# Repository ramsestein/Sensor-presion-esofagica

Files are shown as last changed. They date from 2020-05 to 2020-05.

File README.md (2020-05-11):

# **Open-Source Transpulmonary Pressure Sensor**

Arduino-based Transpulmonary pressure monitoring portable device project:  Open-Source Transpulmonary Pressure Sensor.

This Open-Source Transpulmonary Pressure Sensor (OSTPS) allows for rapid measuring of Transpulmonary Pressure (PL)
through airway pressure (Paw) and esophageal pressure (Pes) capture on intubated patients,
particularly those affected by bilateral pneumonia due to SARS-COV-2, pressures are measured using the respiratory cannula  
for Paw and an esophageal balloon nasogastric probe for Pes.

The OSTPS's accuracy in this first iteration is +-0.18cmH2O (theorical) so its reliability and precision is assumed correct for this type of measurement.

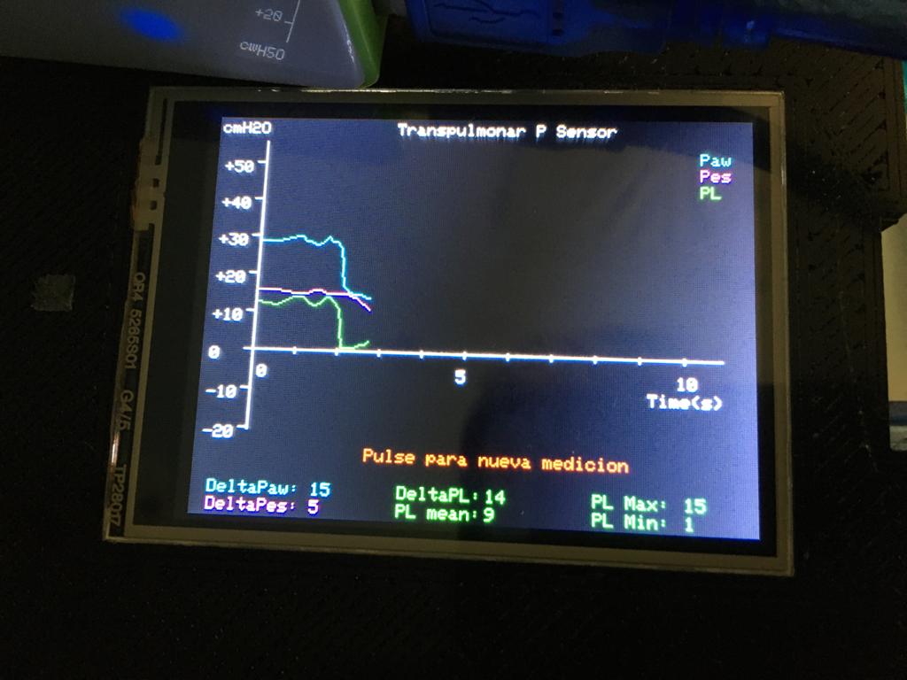
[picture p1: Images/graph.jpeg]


**The use of a OSTPS must be performed by trained medical personnel.**

Mechanical ventilation monitoring, at its basis, encompasses airway pressure and flow.
For most patients, these two measurements are enough to perform ventilation adjustments. 
However, airway pressure is only the resulting measurement of pressures at play in the main respiratory system's components:
lungs and chest wall (simplified).

To perform precise adjustments of mechanical ventilation or evaluating lung recruitability in acutely ill patients,
differentiating these two components compliance is necessary.

It's assumed esophageal pressure (Pes) is representative of pleural pressure*.

Through Paw and Pes measurement it is possible to obtain Transpulmonary Pressure (PL)=Paw-Pes measured
during occlusion at end inspiration and expiration. PL represents the necessary pressure to dilate the lung parenchyma.
This first OSTPS version also calculates Paw and Pes differentials.

Through the use of OSTPS clinicians may get a better perception of patient-ventilator interaction and plan for respiratory strategy
more accurately.

## Problem

PL monitorization is an already existing technology only implemented in most modern mechanical respirators.

Pressure measurements necessary to calculate PL can be obtained with most electromedical devices nonetheless.
Although, this data acquisition without integrated calculation tools is a lengthy process,
demanding a span of time medical personnel can't spare given the high occupancy rate and hard hygiene measures,
as happens with SARS-COV-2 affected patients.

We propose a Transpulmonary Pressure Sensor model, based on Arduino, easy to build and portable.
This prototype can be produced in short time with off the shelf components, and allows medical personnel to correctly asses acutely ill patients,
giving them supplementary room for improvement which may be crucial for recovery in the most critical cases.

The development of this project is based on already existing pressure sensors/transducers, which may be hard to come by given the actual market situation.
We recommend consulting with target medical personnel the need for a OSTPS before sourcing components to avoid a colapse in supply.
Not all medical personnel is familiar with PL monitoring and its implications for mechanical ventilation, this is a fairly recent technique.

Nonetheless this now very accessible technology can help save lives if used correctly,
especially for those acutely ill patients who need more advanced mechanical ventilation monitoring.

### References
1. Talmor D, Sarge T, O’Donnell C, Ritz R, Malhotra, Lisbon A, Loring S. Esophageal and transpulmonary pressures in acute respiratory failure Crit Care Med 2006; 34:1389–1394
2. Gattinoni L, Chiumello D, Carlesso E, Valenza F. Benchto-bedside review: Chest wall elastance in acute lung injury/acute respiratory distress syndrome patients. Critical Care 2004, 8:350-355
3. Hess D, Bigatello L. The chest wall in acute lung injury/acute respiratory distress syndrome. Curr Opin Crit Care 2008;14:94–102
4. Akoumianaki E, Maggiore S, Valenza F, Bellani G, Jubran A, et al. The application of esophageal pressure measurement in patients with respiratory failure. Am J Respir Crit Care Med 2014;189:520-31

### Made possible by
Francisco José Parrilla Gómez - Critical Care Medicine specialist physician, Intensive Medicine Service, Hospital del Mar, Parc de Salut Mar, IMIM, GREPAC, Barcelona - concept, development, clinical advisor, testing  
Andrés Parrilla Gómez - Lycée Saint Stanislas, Nantes - concept, development, programming  
Alvaro Jansà - Fablab Sant Cugat, Barcelona - development, production, programming support  
Marc Estudillo - Electromedical Engineering, Barcelona - development, production  
Victor Boutonnet Antelo - Benimakers Makerspace, Valencia - development, programming support, project coordination  

Made available under Creative Commons Licence Attribution 4.0 International (CC BY 4.0).

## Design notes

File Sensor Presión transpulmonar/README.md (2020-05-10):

# **Sensor de Presión Transpulmonar Open-Source**

Proyecto de herramienta portatil de medición de la presión transpulmonar basada en arduino: Sensor de Presión Transpulmonar Open-source.

El Sensor de Presión Transpulmonar Open-Source (SPTO) permite la rápida medición de la presión transpulmonar (PL)
mediante captación de presión en vía aérea (Paw) y en vía esofágica (Pes) en pacientes intubados,
particularmente afectados de neumonía bilateral por SARS-COV-2, empleando la propía cánula respiratoria  
para la medición de Paw y una sonda nasogástrica con balón esofágico para la medición de Pes.

La precisión del SPTO en su primera versión es de +-0.18cmH2O (teórica) por lo que se comprueba fiabilidad para éste tipo de mediciones.

**El uso del SPTO debe ser realizado por personal médico competente en la materia.**

Aunque técnicamente no sea necesario, éste aparato no ha sido validado por la AEMPS.

La monitorización de la ventilación mecánica comprende como base la presión en vía aérea y el flujo.
Para la mayoría de pacientes, éstas dos medidas son suficientes para realizar los ajustes de ventilación. 
Sin embargo, la Presión en vía aérea es sólo una medición indirecta de las presiones en juego
en los componentes principales del sistema respiratorio (simplificando): pulmones y caja torácia.

Para realizar un ajuste preciso de la ventilación mecánica o evaluar la capacidad de reclutamiento pulmonar de los pacientes más graves,
se hace necesario diferenciar la complianza de ambos.

Está asumido que la medición de la Presión Esofágica (Pes) es un buen indicador que sustituye la medición de la presión pleural*.

Mediante la medición de la Paw y la Pes es posible obtener la presión transpulmonar(PL)=Paw-Pes calculada
durante la oclusión en fin de inspiración y espiración. PL representa la presión necesaria para dilatar el parénquima pulmonar.
El SPTO calcula también los diferenciales de Paw y Pes durante la medición.

De éste modo el personal médico tiene una mejor percepción del efecto de la ventilación mecánica y/o de la capacidad de reclutamiento pulmonar del paciente,
pudiendo realizar ajustes precisos del modo ventilatorio.

*Referencias:
1. Talmor D, Sarge T, O’Donnell C, Ritz R, Malhotra, Lisbon A, Loring S. Esophageal and transpulmonary pressures in acute respiratory failure Crit Care Med 2006; 34:1389–1394
2. Gattinoni L, Chiumello D, Carlesso E, Valenza F. Benchto-bedside review: Chest wall elastance in acute lung injury/acute respiratory distress syndrome patients. Critical Care 2004, 8:350-355
3. Hess D, Bigatello L. The chest wall in acute lung injury/acute respiratory distress syndrome. Curr Opin Crit Care 2008;14:94–102
4. Akoumianaki E, Maggiore S, Valenza F, Bellani G, Jubran A, et al. The application of esophageal pressure measurement in patients with respiratory failure. Am J Respir Crit Care Med 2014;189:520-31

#Problemática:

La monitorización de PL es una tecnología que ya incluyen sólo algunos de los ventiladores mecánicos más modernos.

No obstante, las medidas de presión necesarias al cálculo de PL se pueden tomar con la mayoría de equipos electromédicos ya existentes.
Sin embargo, la toma de medidas sin herramientas de cálculo integradas supone un proceso demasiado largo de toma de datos y procesado de los mismos:
un tiempo del que el personal médico no dispone en situación de alta ocupación sumada a medidas de higiene extremas,
como ocurre con los pacientes afectados por SARS-COV-2.

Proponemos un modelo de sensor de presión transpulmonar, portátil y de fácil fabricación basado en Arduino.
Éste prototipo se puede fabricar en poco tiempo con componentes off the shelf y supone dar capacidad al personal médico para monitorizar los pacientes más graves
dándoles un margen de mejora que puede resultar crucial en los casos más críticos.

El desarrollo está basado en torno a sensores/transductores de presión disponibles en el mercado, aunque difíciles de conseguir en las circunstancias actuales.
Recomendamos consultar con personal médico la necesidad de contar con un SPTO antes de realizar compra de material si se va a fabricar una unidad.
No todo el personal médico está familiarizado con la monitorización de la PL y su implicación para la mecánica respiratoria.

No obstante es una tecnología muy accesible que puede ayudar a salvar vidas si se emplea debidamente,
especialmente en aquellos pacientes más graves que necesitan de una monitorización más avanzada de la ventilación mecánica.

Creado por:
Francisco José Parrilla Gómez - Médico especialista en Medicina Intensiva, Servicio de Medicina Intensiva, Hospital del Mar, Parc de Salut Mar, IMIM, GREPAC, Barcelona - concepto, desarrollo, consejo clínico, pruebas
Andrés Parrilla Gómez - Lycée Saint Stanislas, Nantes - concepto, desarrollo, programación
Alvaro Jansà - Fablab Sant Cugat, Barcelona - desarrollo, producción, soporte programación
Marc Estudillo - Ingeniería electromédica, Barcelona - desarrollo, producción
Victor Boutonnet Antelo - Benimakers Makerspace, Valencia - desarrollo, soporte programación, coordinación proyecto

Liberado bajo Licencia Creative Commons Atribución 4.0 Internacional.

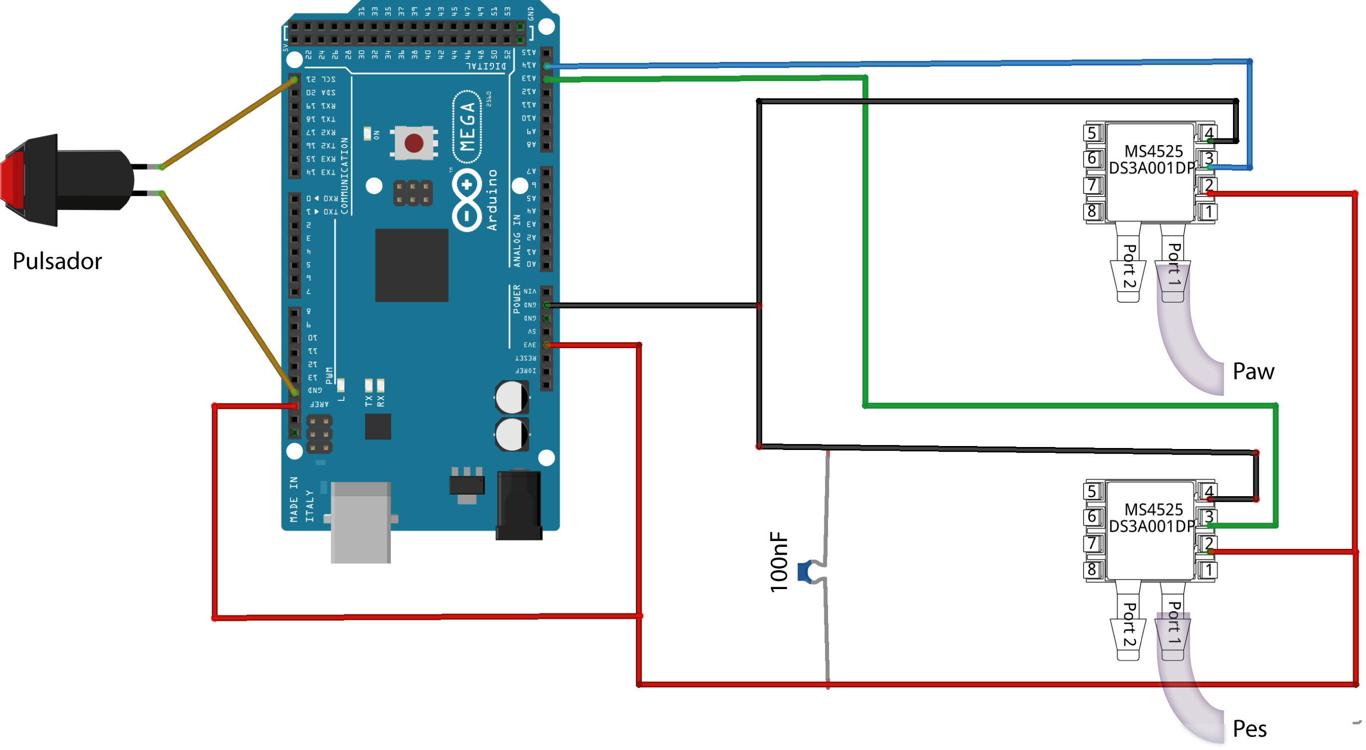
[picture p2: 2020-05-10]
Schematics/Sensor_P_TransP.png

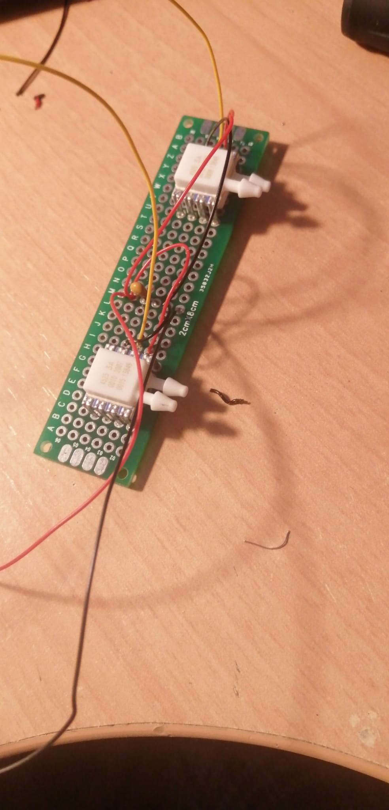
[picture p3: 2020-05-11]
Images/2020-05-01 at 11.52.09.jpeg

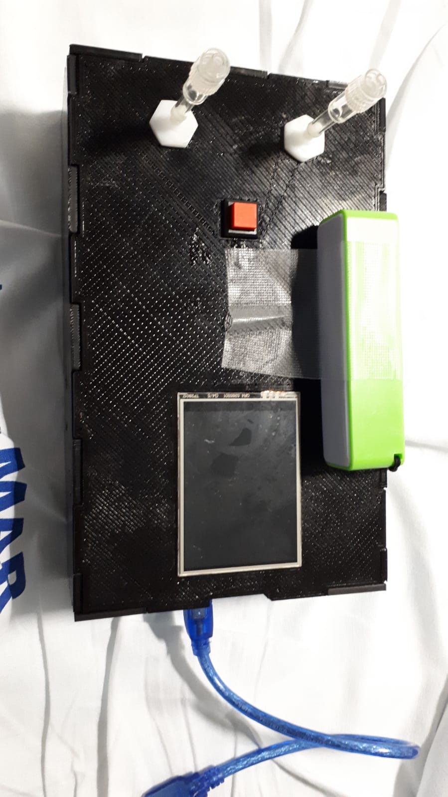
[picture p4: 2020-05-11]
Images/2020-05-06 at 07.55.35.jpeg

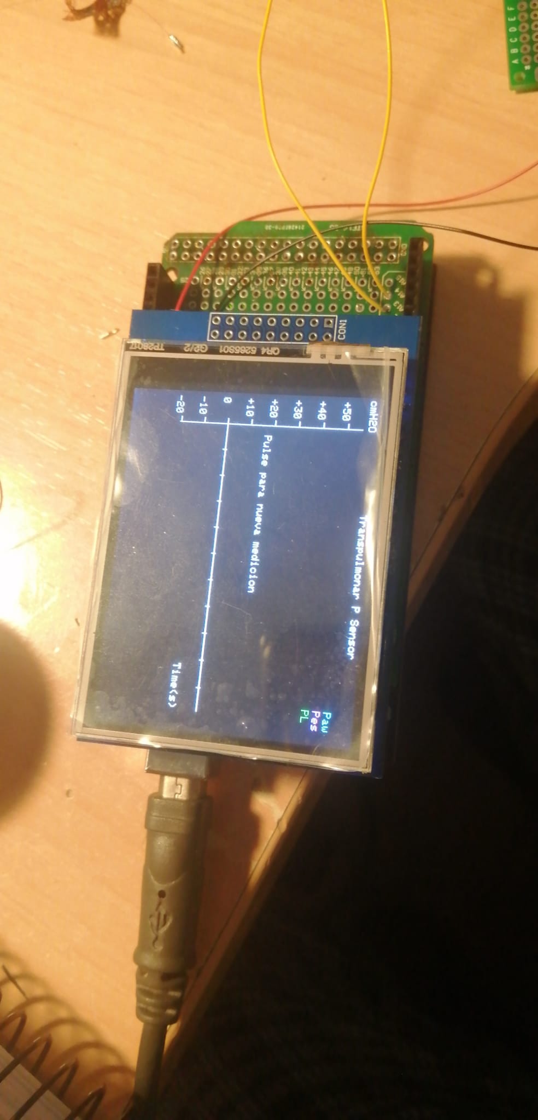
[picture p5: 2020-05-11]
Images/2020-05-01 at 11.52.01.jpeg

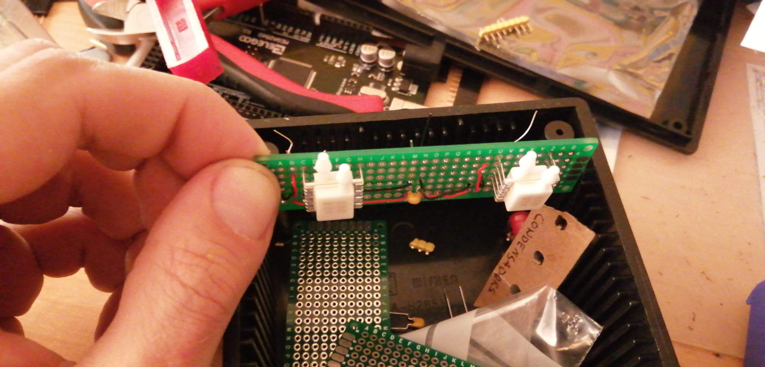
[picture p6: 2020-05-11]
Images/2020-04-30 at 22.00.41.jpeg

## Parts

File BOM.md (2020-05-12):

Arduino Mega    x 1
Arduino Mega Proto Shield Rev3 (PCB)    x 1
Protoshield 3x7cm      x 1
ELEGOO UNO R3 2.8 Inches TFT Touch Screen    x 1
Pulsador     x 1
Capacitador ceramico 100nf     x 1
Sensor presion MS4525     x 2
Tubos XX (interior)     x 2
Adaptadores (int-ext)XX      x 2
Adaptador YY (ext)     x 2

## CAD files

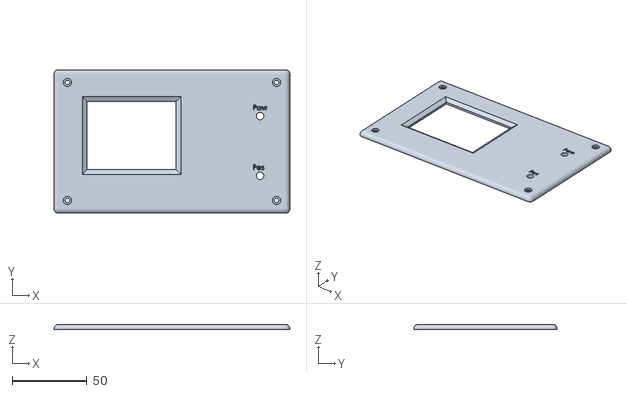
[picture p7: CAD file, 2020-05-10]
CAD/tapa_caja_v0.3.STL
158.0 x 96.0 x 3.50

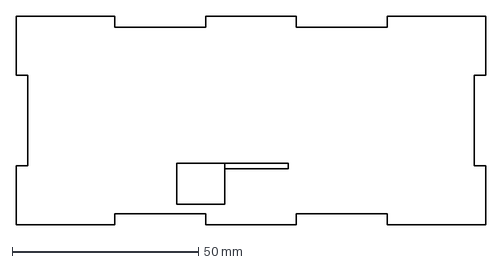
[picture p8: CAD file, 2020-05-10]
CAD/front_makercase_laser_v0.1.DXF
126.0 x 56.0 mm

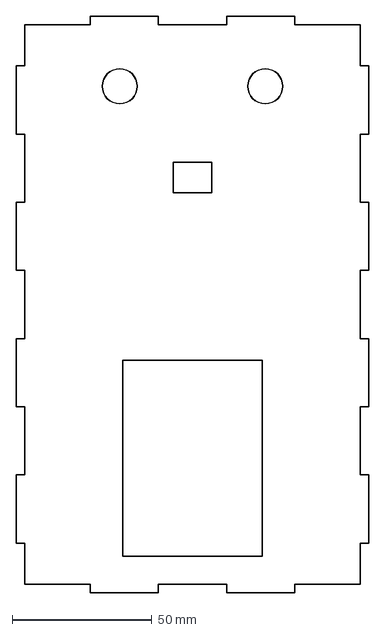
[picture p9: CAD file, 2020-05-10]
CAD/tapa_makercase_laser_v0.1.DXF
126.0 x 206.0 mm

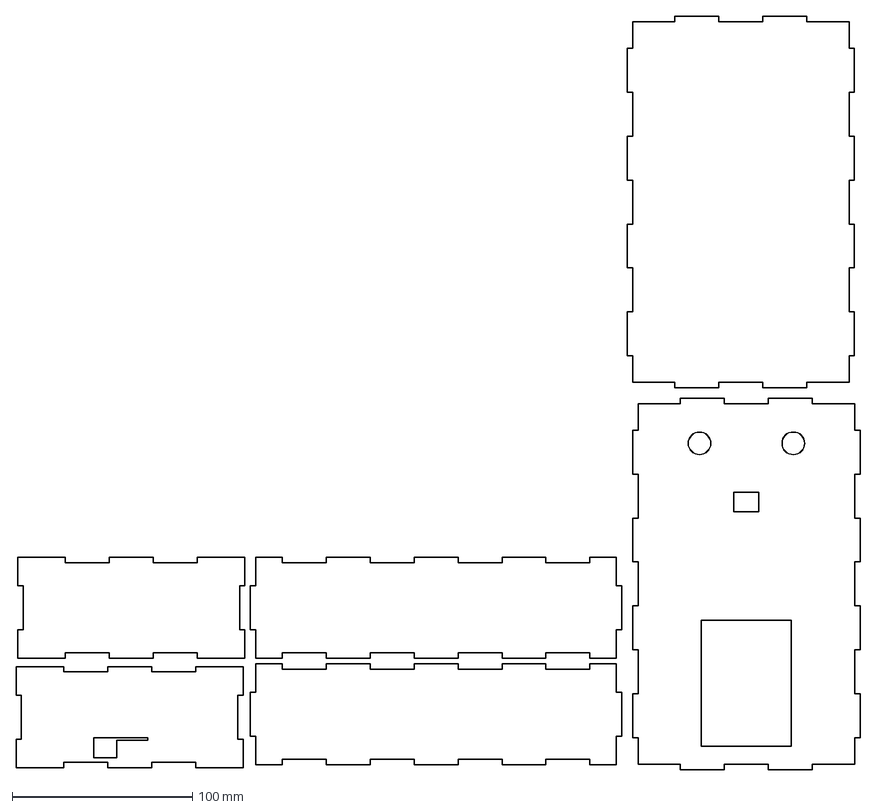
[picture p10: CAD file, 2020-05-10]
CAD/makercase_laser_todo_v0.1.DXF
468.0 x 417.8 mm

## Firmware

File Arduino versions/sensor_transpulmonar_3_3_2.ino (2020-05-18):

/*
Transpulmonar sensor
 version 3.3.4
 
 Authors:
 Francisco Jose PARRILLA GOMEZ
 Alvaro JANSA MAS
 Marc ESTUDILLO
 Victor BOUTONNET ANTELO
 Andres PARRILLA GOMEZ
 
 Description:
 Transpulmonar sensor using 2 pressure sensors, Arduino MEGA and TFT LCL Elegoo 2.8" touchscreen
 
 modifs:
 v1 2020-04-27 : initial version
 v2 2020-04-30 : analog reference to 3.3V, TFT added, compiler options and bug correction
 v3.0 2020-05-02 : graphics improvements
 v3.1 2020-05-02 : bug corrections
 v3.1.1 2020-05-02 : more bug corrections
 v3.1.2 2020-05-03 : graphics improvements
 v3.2 2020-05-04 : graphics improvements
 v3.3 2020-05-04 : round values to integers (round to 0.5 commented out)
 v3.3.1 2020-05.06 : back to float values
 v3.3.2 2020-05.06 : rounding compiler options added
 v3.3.3 2020-05-09 : changed PL avg to Ratio
 v3.3.4 2020-05-09 : bug fix
 */




// User defined compiling parameters
// *********************************
#define ARDUINOBOARD 'M' // must be 'U' for UNO or 'M' for MEGA. Warning: with UNO, fake values!
#define DEBUG 0 // must be 0 or 1
#define USERCOM 'B' // must be 'B' for BUTTON, 'S' for SERIAL or 'T' for TOUCHSCREEN ( TOUCHSCREEN TODO: not working as of 2.6)
#define ROUNDOPTION 0 //must be 1 to integer values, 5 for .5 rounding or 0 for max resolution
// *********************************





// TFT
#include <Elegoo_GFX.h>
#include <Elegoo_TFTLCD.h>
//#include <stdint.h>
#include <TouchScreen.h>

#define LCD_CS A3
#define LCD_CD A2
#define LCD_WR A1
#define LCD_RD A0
#define LCD_RESET A4
#define YP A1
#define XM A2
#define YM 7
#define XP 6

#define GREY    0x8410
#define BLACK   0x0000
#define BLUE    0x001F
#define RED     0xF800
#define GREEN   0x07E0
#define CYAN    0x07FF
#define MAGENTA 0xF81F
#define YELLOW  0xFFE0
#define WHITE   0xFFFF

#define MINPRESSURE 10
#define MAXPRESSURE 1000

#if USERCOM=='S'
#define DEBUG 1
#endif

Elegoo_TFTLCD tft(LCD_CS, LCD_CD, LCD_WR, LCD_RD, LCD_RESET);
#if USERCOM=='T'
TouchScreen ts = TouchScreen(XP, YP, XM, YM, 300);
#endif

// Pin definitions
#if ARDUINOBOARD=='M'
const int PesPin(A13);
const int PawPin(A14);
#endif

#if USERCOM=='B'
const int buttonPin = 21; // Warning, I2C pin too...
unsigned long timeButton(0);
#endif

// Sensors characteristics
int PesVDefaultOffset(512);
int PawVDefaultOffset(512);
int PesVOffset(PesVDefaultOffset); 
int PawVOffset(PawVDefaultOffset);

// gain definitions for class A TE sensors (MS4525 - DS3A001DP)
//for 3V supply and AREF=3.3V
float PesGain(70.31/409); //1 psi = 70,31 cmH2O
float PawGain(70.31/409);

//Data treatment parameters
int nMeasures(10); // number of measures to average (low-cost filtering...)
float precision(0.);
int tmp(0.);

//current values
int PesV(0); // V stands for Volts (direct tension measured)
int PawV(0);
int PesVtmp(0);
int PawVtmp(0);
int PesVmax(0);
int PesVmin(1023);
int PawVmax(0);
int PawVmin(1023);
float Pes(0.);
float Paw(0.);
float PL(0.);
float PLmax(0.);
float PLmin(0.);
float PLavg(0.);
float Pesmax(0.);
float Pesmin(0.);
float Pawmax(0.);
float Pawmin(0.);
int counterMeasures(0);

// behavior variables
bool measuring=false;
//TSPoint tcPoint;

// plotting variables
int HPos (31+250); // pixel corresponding to time=0 + plotting area width
int lastHPos(31+250);

unsigned int Pes2plot(0);
unsigned int Paw2plot(0);
unsigned int PL2plot(0);
unsigned int lastPes2plot(0);
unsigned int lastPaw2plot(0);
unsigned int lastPL2plot(0);

// time variables
float tini(0); //measure start time
float tcurrent(0); //measure start time
int screenNumber(0); // times screen erased and shown again (multiples of 10s)

void setup() {

  // Touchscreen ini
  tft.reset();
  tft.begin(0x9341);
  tft.fillScreen(BLACK);
  tft.setRotation(1);

#if DEBUG==1 || USERCOM=='U'
  Serial.begin(9600);
  pinMode(13,OUTPUT);
  digitalWrite(13,LOW);
#endif

#if USERCOM=='B'
  pinMode(buttonPin, INPUT_PULLUP);
#if ARDUINOBOARD=='M'
  attachInterrupt(2, buttonPressed, FALLING); // 2 stands for pin 21 (number 2 of Mega board interrupts)
#elif ARDUINOBOARD=='U'
  tft.fillScreen(BLACK);
  tft.setCursor(40,100);
  tft.println("ERROR:Opotions defined are not compatible (UNO board with BUTTON communication");
#endif
#endif



  // Pressure sensors autozero
  analogReference(EXTERNAL);
#if ARDUINOBOARD=='M'
  pinMode(PesPin, INPUT);
  pinMode(PawPin, INPUT);
#endif

  PesVtmp=0;
  PawVtmp=0;
  PesVmax=0;
  PesVmin=1023;
  PawVmax=0;
  PawVmin=1023;
  PesVOffset=0;
  PawVOffset=0;
  for(int i = 0; i < nMeasures; i++){
#if ARDUINOBOARD=='M'
    PesVtmp=analogRead(PesPin);
    PawVtmp=analogRead(PawPin);
#elif ARDUINOBOARD=='U'
    PesVtmp=512+int(random(-3,4)); //UNO fake values
    PawVtmp=520+int(random(-3,4)); //UNO fake values
#endif
    PesVOffset+=PesVtmp;
    PawVOffset+=PawVtmp;
    PesVmax=max(PesVmax,PesVtmp);
    PesVmin=min(PesVmin,PesVtmp);
    PawVmax=max(PawVmax,PawVtmp);
    PawVmin=min(PawVmin,PawVtmp);
    delay(10);
  }
  PesVOffset=PesVOffset/nMeasures;
  PawVOffset=PawVOffset/nMeasures;

#if DEBUG==1
  Serial.println("AUTOZERO");
  if(abs(PesVOffset-PesVDefaultOffset)>50){
    Serial.print("Warning: check autozero for Pes");
  }
  Serial.println("PesVOffset="+String(PesVOffset));
  if(abs(PawVOffset-PawVDefaultOffset)>50){
    Serial.print("Warning: check autozero for Paw");
  }
  Serial.println("PawVOffset="+String(PawVOffset));
  if(PesVmax-PesVmin>50){
    Serial.print("Warning: instable measures of Pes: max="+String(PesVmax)+" ; min="+String(PesVmin));
  }
  if(PawVmax-PawVmin>50){
    Serial.print("Warning: instable measures of Paw: max="+String(PawVmax)+" ; min="+String(PawVmin));
  }
#endif

  tft.setCursor(20,100);
  tft.setTextColor(WHITE);
  tft.setTextSize(2);
  tft.println("Autozero done");
  tft.setCursor(20,120);
  tft.setTextSize(1);
  precision=max(max(PesGain*float(PesVmax-PesVmin),PawGain*float(PawVmax-PawVmin)),0.2);
  tft.println("precision:+- "+String(round(precision*10.)/10)+"."+String(round(precision*10.)%10)+" cmH2O");
#if DEBUG==1
  Serial.print("PesVmax: ");
  Serial.println(PesVmax);
  Serial.print("PesVmin: ");
  Serial.println(PesVmin);
  Serial.print("PawVmax: ");
  Serial.println(PawVmax);
  Serial.print("PawVmin: ");
  Serial.println(PawVmin);
  Serial.print("precision: ");
  Serial.println(precision);
  Serial.print("round(precision*10.)/10: ");
  Serial.println(round(precision*10.)/10);
  Serial.print("round(precision*10.)%10: ");
  Serial.println(round(precision*10.)%10);
#endif
  delay(2000);
  tft.fillScreen(BLACK);

  //X Y Axis
  tft.fillRect(30,15,1,176,WHITE); // Y
  tft.fillRect(30,143,272,1,WHITE); // X

  //graph key
  tft.setCursor(290,30);
  tft.setTextColor(MAGENTA);
  tft.setTextSize(1);
  tft.println("Pes");

  tft.setCursor(290,20);
  tft.setTextColor(CYAN);
  tft.setTextSize(1);
  tft.println("Paw");

  tft.setCursor(290,40);
  tft.setTextColor(GREEN);
  tft.setTextSize(1);
  tft.println("PL");


  //X axis divider
  for(int i=56;i<=281;i+=25){
    tft.drawLine(i,142,i,145,WHITE);
  }
  //Y axis divider
  //tft.drawLine(25,15,30,15,WHITE); // 60cmH2O
  tft.drawLine(25,28,30,28,WHITE); // 50cmH2O
  tft.drawLine(25,51,30,51,WHITE); // 40cmH2O
  tft.drawLine(25,74,30,74,WHITE); // 30cmH2O
  tft.drawLine(25,97,30,97,WHITE); // 20cmH2O
  tft.drawLine(25,120,30,120,WHITE); // 10cmH2O
  tft.drawLine(25,143,30,143,WHITE); // 00cmH2O
  tft.drawLine(25,166,30,166,WHITE); // -10cmH2O
  tft.drawLine(25,189,30,189,WHITE); // -20cmH2O

  tft.setTextColor(WHITE);
  tft.setTextSize(1);

  tft.setCursor(110,3);
  tft.println("Transpulmonar P Sensor ");

  tft.setCursor(2,3);
  tft.println("cmH2O");

  tft.setCursor(260,163);
  tft.println("Time(s)");

  // Y scale
  tft.setCursor(5,28);
  tft.println("+50");

  tft.setCursor(5,51);
  tft.println("+40");

  tft.setCursor(5,74);
  tft.println("+30");

  tft.setCursor(5,97);
  tft.println("+20");

  tft.setCursor(5,120);
  tft.println("+10");

  tft.setCursor(5,143);
  tft.println("0");

  tft.setCursor(5,166);
  tft.println("-10");

  tft.setCursor(5,189);
  tft.println("-20");

}
void loop() {

  // reset max, min, average values
  PLmax=-100;
  PLmin=100;
  Pesmax=-100;
  Pesmin=100;
  Pawmax=-100;
  Pawmin=100;
  PLavg=0;
  counterMeasures=0;

  tft.fillRect(90,198,200,10,BLACK);
  tft.setCursor(100,200);
  tft.setTextColor(RED);
  tft.println("Pulse para nueva medicion"); //"tap for new measuring"
  tft.setTextColor(WHITE);

  while(!measuring){
#if DEBUG==1
    Serial.println("waiting");
#endif
#if USERCOM=='S'
    if (Serial.available() > 0) {
      char inChar = (char)Serial.read(); 
      if (inChar == 'a') {
        measuring=true;
      }
    }
#elif USERCOM=='T'
    TSPoint tcPoint = ts.getPoint();
    //Serial.println(tcPoint.z);
    if (tcPoint.z > MINPRESSURE && tcPoint.z < MAXPRESSURE) {
      measuring=true;
      //Serial.println("start");
    }
#elif USERCOM=='B'
    // coded in interrupt function
#else
    tft.fillScreen(BLACK);
    tft.setCursor(40,100);
    tft.println("ERROR:No communication defined");
#endif
    delay(100);

  }
#if DEBUG==1
  digitalWrite(13,HIGH);
  Serial.println("starting measures");
#endif

  //starting time
  tini=millis()/1000.; //measure start time
  doMeasure(Pes,Paw,PL);
  Pes2plot=map(Pes,0,50,143,28);
  Paw2plot=map(Paw,0,50,143,28);
  PL2plot=map(PL,0,50,143,28);
  HPos=31+250;
  ;

  //restart screen
  tft.fillRect(31,0,280,215,BLACK); // plot
  tft.setCursor(110,3);
  tft.fillRect(0,198,320,50,BLACK); //max, min data
  //tft.println("Transpulmonar P Sensor ");
  tft.fillRect(33,185,320,100,BLACK);
  tft.fillRect(30,143,272,1,WHITE); // X
  screenNumber=0;  

  tft.setCursor(290,30);
  tft.setTextColor(MAGENTA);
  tft.setTextSize(1);
  tft.println("Pes");

  tft.setCursor(290,20);
  tft.setTextColor(CYAN);
  tft.setTextSize(1);
  tft.println("Paw");

  tft.setCursor(290,40);
  tft.setTextColor(GREEN);
  tft.setTextSize(1);
  tft.println("PL");

  // Loop : measurements until interaction
  while(measuring){ // measuring should change on interaction (touchscreen or button click, serial com)

    // store former values
    lastPes2plot=Pes2plot;
    lastPaw2plot=Paw2plot;
    lastPL2plot=PL2plot;
    lastHPos=HPos;

    tcurrent=millis()/1000.-tini;
    HPos=31+long(tcurrent*25.)%250; //TODO to improve and verify...



    if(long(tcurrent)/10 +1 > screenNumber){ // create new screen
      screenNumber++;
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

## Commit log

2020-05-09 Upload New File
    [front_makercase_laser_v0.1.DXF]
2020-05-10 Deleted doc/Oximetro_coronavirusmarkers_MonitorPulsoSpO2.pdf, pcbs/README, src/backend/config/default.yml, src/backend/database/ER.pdf, src/backend/database/VitalOx.sql, src/backend/database/delete-d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
2020-05-10 Update CAD/.gitkeep, CAD/front_makercase_laser_v0.1.DXF, CAD/makercase_laser_todo_v0.1.DXF, CAD/tapa_caja_v0.3.STL, CAD/tapa_makercase_laser_v0.1.DXF, Arduino versions/.gitkeep, Arduino versions/sens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
    [front_makercase_laser_v0.1.DXF, makercase_laser_todo_v0.1.DXF, tapa_caja_v0.3.STL, tapa_makercase_laser_v0.1.DXF]
2020-05-10 Deleted Sensor Presión transpulmonar/.gitkeep
2020-05-17 Replace sensor_transpulmonar_3_3_2.ino with 3_3_4 version
